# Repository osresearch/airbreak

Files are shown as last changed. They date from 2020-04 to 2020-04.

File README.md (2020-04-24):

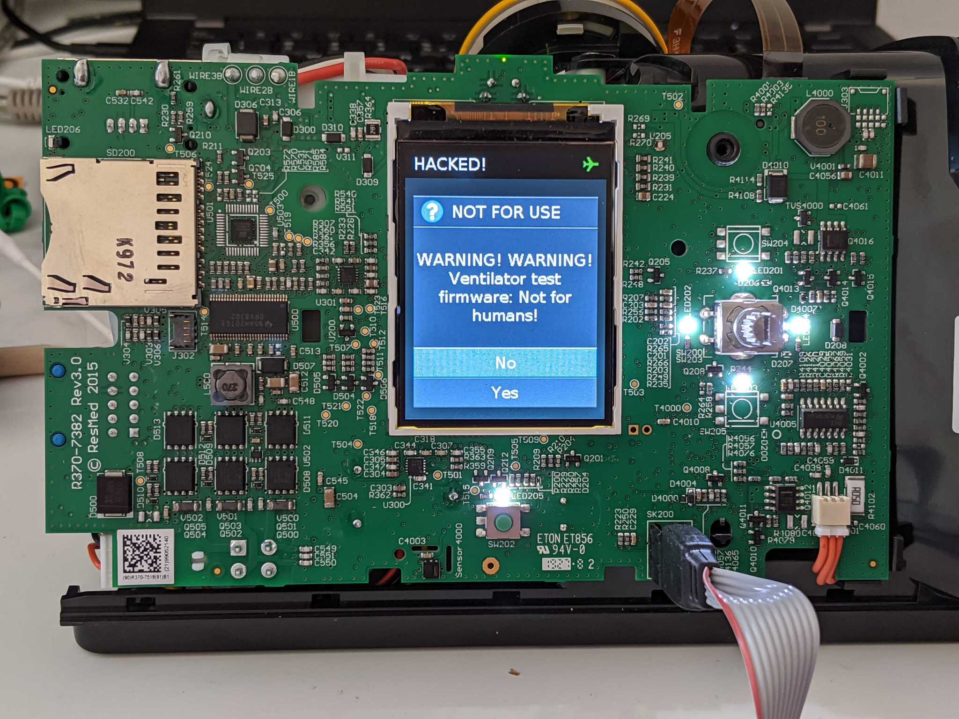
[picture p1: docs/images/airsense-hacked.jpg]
CPAP running custom firmware

# Jailbreaking CPAP machines to make temporary ventilators

This is the README for the internals of ResMed CPAP jailbreak works;
for a high-level overview, see [airbreak.dev](https://airbreak.dev).
The project is [MIT licnsed](LICENSE.txt) and has a [CoC](CODE_OF_CONDUCT.md).
Please review the [Contributor's Guidelines](CONTRIBUTORS.md) before
submitting issues or pull requests.

**This tree does not contain any files that are copyrighted by ResMed.**
You must have a device to extract the firmware from, which is then patched,
and the modified version is re-flashed.

You will need the tools described in [docs/disassembly](docs/disassembly.md).
The `stubs.S` file that has been committed is for SX567-0401. Flashing it on
a different version will likely cause problems.

Extensions can either replace existing functions at fixed addresses,
or can use some of the unused space in the image.
The `Makefile` has a short explanation of how to do this; the
`patch-airsense` file will also need to be updated to patch the
binary file into the firmware.

# Helpful GDB commands:

Start `gdb`, connect to the OpenOCD server and disassemble the current address:
```
gdb-multiarch -iex 'target remote localhost:3333'
display/i $pc
```

Reboot the device and halt before running any code:
```
mon reset halt
```

Unlock the STM32 and flash the new firmware into it:
```
mon stm32f2x options_write 0 0x2c ; reset halt ;  flash write_image erase stm32-unlocked.bin 0x8000000
```

Read the Therapy Manager floating point variables, or a specific one like the target
pressure (`0x2d`):
```
x/200f 0x2000e948
x/f (0x2000e948 + 4 * 0x2a)
```

Read the Therapy Manager integer variables, or a specific one like the current mode (`0x6F`):
```
x/200xw 0x2000e750
x/xw (0x2000e750 + 4 * 0x6F)
```

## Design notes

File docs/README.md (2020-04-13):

CPAP running custom firmware
# Airbreak: jailbreak your CPAP device

In light of the COVID-19 crisis and resultant shortage of medical equipment,
[hospitals have been using BiPAP (BIlevel Positive Airway Pressure) machines as non-invasive ventilators](https://health.mountsinai.org/blog/mount-sinai-turns-hundreds-of-machines-for-sleep-apnea-into-hospital-ventilators-shares-instructions-worldwide/),
and [several groups](https://github.com/PubInv/covid19-vent-list) are currently working on ventilator designs that involve a converted BiPAP.
CPAP devices are cheaper, more widely available, and similar electrically and mechanically. However, they are lacking in some features that the physicians require and,
according to their manufacturer, CPAP machines "[*would require significant rework in order to function as a ventilator*](https://www.resmed.com/en-us/covid-19/)".
other respiratory disorders.

What we have done it to "*jailbreak*" the the Airsense 10 CPAP (Constant
Positive Airway Pressure) machine, a common, low-cost sleep therapy device
intended to treat sleep apnea, so that it is possible to run additional
tasks on the device to add the features necessary to use the device as
a temporary ventilator.  This can help ease the shortage until more real
ventilators are available.

Our changes bring the Airsense S10 to near feature parity with BiPAP
machines from the same manufacturer, boost the maximum pressure output
available, and provide a starting point to add more advanced emergency
ventilator functionality.

## Disclaimer

While we are consulting with doctors to validate that the modified
firmware works as intended, the codebase in its current form should
be considered a proof of concept and is not intended for use in a
life-support capacity.  Please see the [FAQ](#FAQ) for more information.

No IP belonging to the device manufacturer is hosted in this repository,
nor will it be accepted as a pull request.

## Major features:
* Adds a timed breathing mode that oscillates between high and low pressure (stock firmware is only a single pressure)
* Allows maximum pressure to be increased to 30 cm H2O (stock firmware is 20cm H2O)
* Allows very smooth rapid pressure change rates (stock firmware ramps 1 cm/sec)
* Unlocks all of the vendor modes and tunable configuration parameters
* Access to all of the sensors (flow, pressure, temperature, etc)
* Reads tuning parameters from a memory location accessible over SWD
* Real-time data export over SWD
* Real-time graphs on the screen to show an immediate history of data

## Features under development:
* Closed loop air pressure control with backup respiration rates ("VAPS" mode)
* Visual and audible alarms when flow stoppage or leakage rates are detected
* GPIO interface with other systems

# FAQ

## What's the difference between the CPAP and BiPAP machines?
The Airsense 10 that we have modified is a low cost sleep therapy device that
provides a *Constant* air pressure to help with sleep apnea and other disorders.
The BiPAP machines can produce two levels of pressure, which allows them to
be used a temporary ventilators.  Adding a function to the existing firmware
that alternate between pressures allows the CPAP to effectively function
similar to a BiPAP system.

## Can this be used to treat COVID patients?
We want to be very clear here: this modified firmware should not be
flashed on CPAP machines and used to treat COVID patients immediately.
The firmware that we've developed is an effective demonstration of
the capability, and while it has been reviewed and validated by expert
researchers, biomedical engineers, and clinical pulmonologists, it has
not yet been put through FDA approval.  Additionally, the
[Mt Sinai's protocols for off-label non-invasive ventilation](https://health.mountsinai.org/wp-content/uploads/sites/14/2020/04/NIV-to-Ventilator-Modification-Protocol-v1.02-for-posting.pdf)
require additional modifications such as viral filter and remote control
before the machines are ready for clinical use.

## Could this sort of hack alleviate the shortage of ventilators?
If the manufacturers developed their own firmware updates, or the FDA
approves the jailbroken ones, this could have an extremely large role
in bridging the ventilator shortage gap.
There are millions of unused or underutilized CPAP and BiPAP devices sitting in
closets in America, and roughly another 500,000 units in warehouses in
the country.  These devices can be used as an alternate ventilator, for
low-resource hospitals who are still waiting for the hospital ventilators
to arrive.

## Could this go through FDA approval?
If there were no other option it could, but we believe that the best
route for rolling out these upgrades is to work with the manufacturers
to use their resources to validate and distribute these upgrades safely
and at scale.  There are three main factors at play here:

* The first is a regulatory/safety one:  Under the recently-released
FDA guidance on hardware and software modification of CPAP and BiPAP
devices to treat COVID patients, the manufacturer has a carte blanche
to release an updated version of their firmware for their own devices
without requiring explicit FDA approval -- they are in the best position
from a technical, expertise, safety and regulatory perspective.

* The second is a practical one:  There are lots of different models of
CPAP and BiPAP devices, and reverse-engineering is a slow and painful
process. We modified the most common model of CPAP in America, but to
get lots of ventilators quickly, you'd need a firmware modification for
every mode of CPAP. What we've found in our work is that the work needed
for the manufacturer to implement these upgrades is pretty minimal --
the manufacturer has access to the source code, to the schematics,
and to the engineers who are intimately familiar with physiology and
safety standards.  We've found that, in many cases, the bulk of the
work is already done and through FDA, like the iVAPS menu that
is in the firmware on the ResMed Airsense device.  Even if other
manufacturers had not written a line of code for their CPAP models, the
simple pressure-control ventilator mode that we were able to implement
is very simple to develop, is designed to work on every CPAP device in
existence, and would be a very low technology and regulatory barrier
for manufacturers who have the right people and resources.

* The third is related to making these jailbreaks at scale:  We could take
in every unused CPAP device in the country, [unscrew the case and
re-flash the firmware](Installation).  It's slow and expensive but could
be solved with lots and lots of people.  The thing is, of the 8 million
CPAPs in the country, almost all 5 million shipped over the last 3 years
have a cellular IoT connection that is always on, reporting back usage
information to the doctors and the insurance companies.  That cellular
connection also has over-the-air upgrade capability that can only be
accessed from within the IT infrastructure of the device manufacturers.
This is a big deal -- it means that they can selectively upgrade, by
serial number, specific units to function as ventilators, without having
to open them up -- it can all work over the air.

## So what's the point?
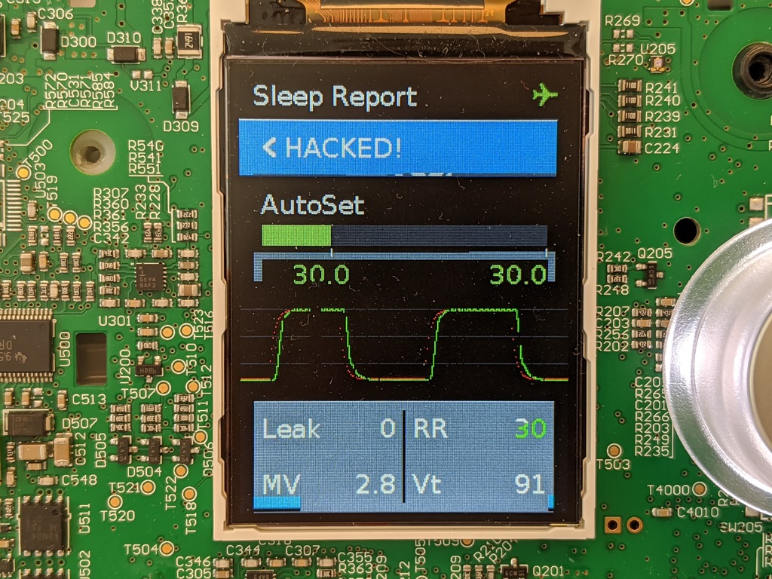
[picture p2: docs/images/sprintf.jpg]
Onscreen graphs


What our firmware does is show that it is possible to re-program these
devices in a way that doctors can use to effectively ventilate COVID
patients. We have been able to confirm the functionality of the devices
in instrumented patient circuits operated by experts in pulmonological
measurement. And there are doctors who agree that, if they had an
FDA-approved machine that could that can do what these machines are doing,
then they could use them to clinically ventilate COVID patients in an ICU.

We do have a path to get this firmware through FDA, and we would apply for
FDA approval under the Emergency Use Authorization if the manufacturers
absolutely refused to cooperate, but the safest and best path is for
the manufacturers to enable this upgrade on their own.

Device owners can also use these tools to write their own [extensions to customize
their devices for their needs](info/extensions), similar to [Magic Lantern](https://magiclantern.fm)
for cameras, as well as the better understand their own therapy by gaining
access to the sensors on the device.  They can add features like the on-screen
graphs shown above, or integrate external systems through the expansion port.

# Evaluation

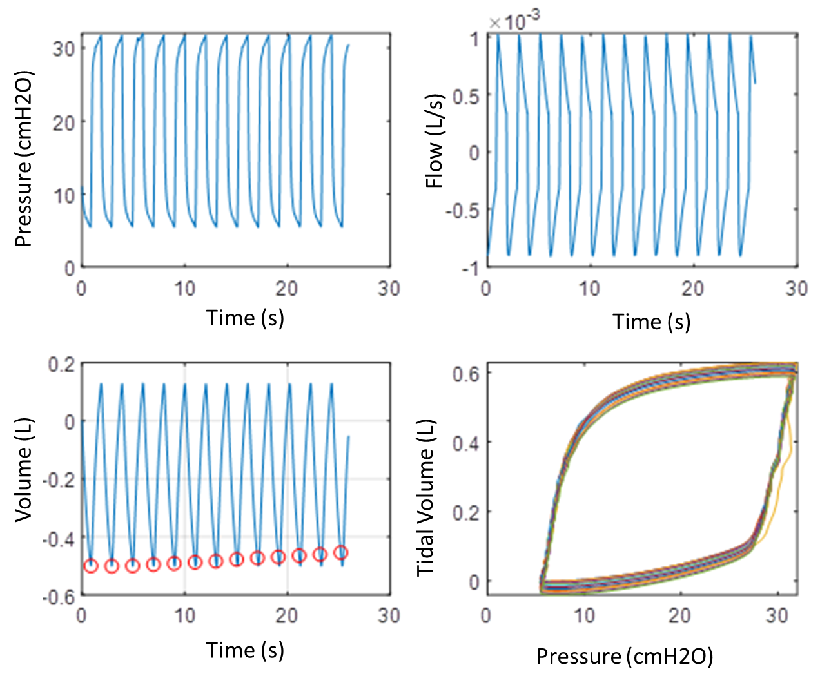
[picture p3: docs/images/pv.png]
PV curves


To be written.  Currently the modified firmware is being evaluated by
research labs and pulmnologists.  There are other pieces necessary to
use the devices in a clinical setting, such as filter traps, O2 inputs,
alarms, etc.

[Mt Sinai's BiPAP protocols for non-invasive ventilation](https://health.mountsinai.org/wp-content/uploads/sites/14/2020/04/NIV-to-Ventilator-Modification-Protocol-v1.02-for-posting.pdf)
provide a roadmap for how these modified CPAP devices could be used.

# More details

* [Installation guide](/disassembly)
* [Writing extensions](info/extensions)

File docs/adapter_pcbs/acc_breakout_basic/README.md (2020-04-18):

# Accessory Board Edge Connector Breakout

Small PCB that fits into the accessory port on the side. Originally designed for building out the monitor USART connection.

This board is designed to be millable on a Bantam PCB mill so makes some odd-looking PCB design choices. As there is no PTH you'll notice headers were put on each side in photo below. You will need to use both 1/32" and 1/64" end mills.

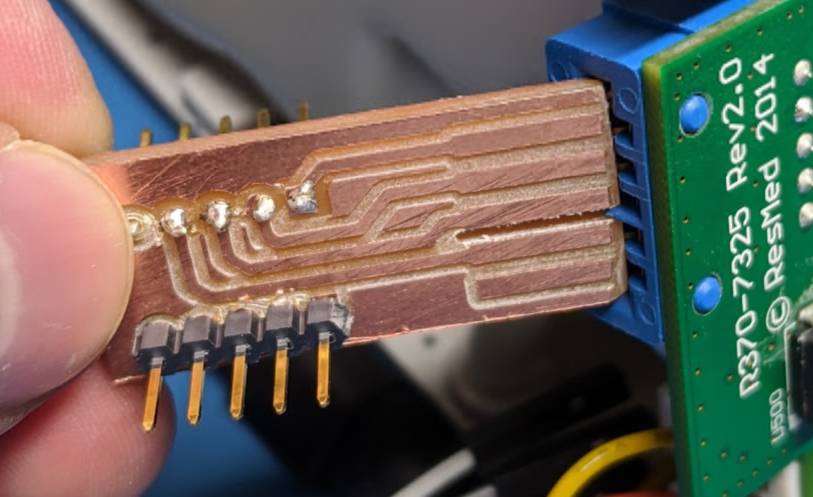
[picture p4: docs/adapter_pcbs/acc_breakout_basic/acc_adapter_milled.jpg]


You can freely send the board away to be made of course too.

**WARNING**: Sanding FR4 material creates dangerous dust. If you need to bevel the edge use appropriate precautions such as sanding under water.

## PCB Source Format

PCB design files are in Altium Designer source (sorry).

### Sizes

The card edge dimensions are roughly based on a standard card-edge, see [example connector spec that includes PCB sizes](https://media.digikey.com/pdf/Data%20Sheets/Panasonic%20Electric%20Works%20PDFs/AXC.pdf).

Board should be 15 mm width (or a little less). The gerber files have a small board outline width to ensure Bantam software gives correct edge size (otherwise may mill on outside edge).

The connectors are on 2.54mm (0.100" grid). Other spacing shown below:

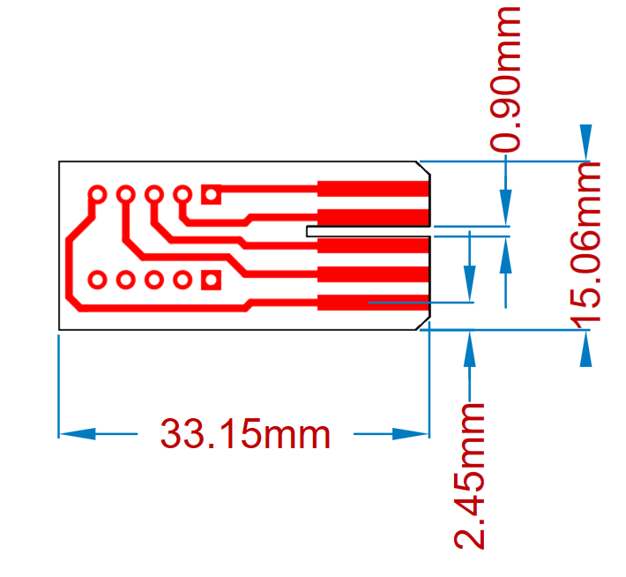
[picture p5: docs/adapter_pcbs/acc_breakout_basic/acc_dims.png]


## Pinout Notes

See pinout stored in rest of project, the following shows pinout of hedaers relative to pin numbers marked on main-board part number:

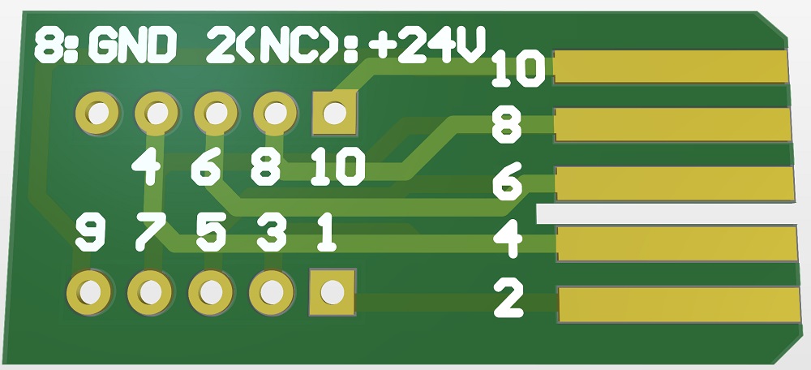
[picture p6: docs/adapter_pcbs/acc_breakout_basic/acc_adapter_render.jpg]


Note that pin 2 is +24V and is NOT connected to the header. Add the wire if you need it, but assumed more people will be sad-face about brushing +24V against their 3.3V USART adapter than would use the +24V for debug.

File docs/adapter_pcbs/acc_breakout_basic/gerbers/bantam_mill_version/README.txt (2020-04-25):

These gerbers are designed to work with the Bantam mill.

They use 2.3 format, with very small edge (GM1) layer.

You will need 1/32" and 1/64" end mills to mill this.

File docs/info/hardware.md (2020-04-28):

# Airsense S10 Hardware

This page aggregates hardware details about the Airsense S10 electronics
and other information that may be relevant to the reverse engineering process.

## FCC Filings

One crucial reverse engineering resource is the
[FCC documentation for the AirSense S10](https://fccid.io/2ACHL-AIR104G), which
includes external and internal schematics and user manuals.

[The FCC filings for the AirCurve BiPAP](https://fccid.io/2ACHL-A10STA3G),
currently in use as an emergency ventilator, shows very similar electronics.

## Clinical Manuals

[Clinical manuals](https://www.manualslib.com/brand/resmed/medical-equipment.html)
for the assisted-breathing devices from this manufacturer provide a great deal
of insight into the various models in the AirSet and AirCurve lines, as well as
the ventilation features available in each one.
Many of the menu options restricted to other models can be enabled by flipping
configuration bits in the firmware.

## Components 

Here are some of the components on the AirSense S10 

Main PCB

| Part  		| Part No. | Manufacturer | Reference | Additional |
| ---			| --- | --- | --- | --- |
| Main uC		| STM32F405ZGT6 (LQFP144) | STMicroelectronics | [Datasheet](https://www.st.com/resource/en/datasheet/stm32f405zg.pdf) | [Reference Manual](https://www.st.com/resource/en/reference_manual/cd00190271-stm8s-series-and-stm8af-series-8bit-microcontrollers-stmicroelectronics.pdf) | 
| Aux uC		| STM8S005 (TQFP48) |  STMicroelectronics | [Datasheet](https://www.st.com/content/ccc/resource/technical/document/datasheet/21/5a/57/8b/f4/49/4a/12/DM00037613.pdf/files/DM00037613.pdf/jcr:content/translations/en.DM00037613.pdf)  | [Reference Manual](https://www.st.com/resource/en/reference_manual/cd00190271-stm8s-series-and-stm8af-series-8bit-microcontrollers-stmicroelectronics.pdf) | 
| Power watchdog IC	| POWR605  | Lattice | [Datasheet](http://www.latticesemi.com/~/media/LatticeSemi/Documents/DataSheets/ProcessorPM-POWR605DataSheet.pdf) | Monitors pressures - see notes below|
| Main Pressure Sensor  | NPA-300M-015A | Amphenol | [Datasheet](https://amphenol-sensors.com/en/component/edocman/212-novasensor-npa-surface-mount-pressure-sensors-datasheet/download?Itemid=8429) | Operates in analog mode |
| Differential Pressure Sensor | SDP8xx | Sensirion | [Datasheet](https://www.sensirion.com/en/about-us/company/technology/cmosens-technology-for-gas-flow/) | Digital mode, manifold mount |
| Programming Header	| TC2050-IDC | Tag-Connect LLC | [DigiKey](https://www.digikey.com/product-detail/en/tag-connect-llc/TC2050-IDC/TC2050-IDC-ND/2605366) | 
| Motor Driver | DRV8302 | Texas Instruments | [DigiKey](https://www.digikey.com/product-detail/en/tag-connect-llc/TC2050-IDC/TC2050-IDC-ND/2605366) | 
| Serial EEPROM | M95M02 | STMicroelectronics | [Datasheet](https://www.st.com/resource/en/datasheet/m95m02-dr.pdf) | 
| LCD | TM024HDZ29 | Tianma | [Similar datasheets](https://www.beyondinfinite.com/product/lcd/tianma_lcd_display.html) | [Closest we could find](https://z3d9b7u8.stackpathcdn.com/pdf-down/T/M/0/TM024HDH30-01-Tianma.pdf)|
| Relay Driver | A2550 | Allegro | [Datasheet](https://www.allegromicro.com/~/media/Files/Datasheets/A2550-Datasheet.ashx) | Function unknown; accessory? | 
| Logic Voltage Regulator (x2) | ISL9000A | Renesas | [Datasheet](https://www.mouser.ca/datasheet/2/698/isl9000a-1529533.pdf) | Generates 3.3v and 5v logic voltages | 
| Top Switch | B3F-3125 | Omrom | [Digikey](https://www.digikey.com/product-detail/en/omron-electronics-inc-emc-div/B3F-3125/SW851-ND/368368) | In case switch needs to be replaced (confirmed exact fit)|

Cellular Module & Antenna (CAM) Board

| Part  		| Part No. | Manufacturer | Reference | Additional |
| ---			| --- | --- | --- | --- |
| Main uC		| R5F5210ABDFP | Renesas | [Datasheet](https://www.renesas.com/eu/en/doc/products/mpumcu/doc/rx_family/r01ds0041ej0150_rx210.pdf) | LFQFP 100-pin |
| CDMA Radio Module| ce910-dual | Telit | [Datasheet](https://static6.arrow.com/aropdfconversion/1e95506f859937cecfcd3d7fd07cc25d6eab906d/telit_ce910-dual_datasheet.pdf) | [qualcomm qsc1105 chipset](https://fccid.io/RI7CE910-DUAL/Internal-Photos/Internal-Photos-1760716) |
| 3G Radio Module| HE910-D | Telit | [Datasheet](hhttps://www.telit.com/wp-content/uploads/2017/09/160229_DS_HE910.pdf) | [Uknown chipset- FCC photos obscured](https://fccid.io/RI7HE910/Internal-Photos/Internal-Photos-1654391)|
| 4G Radio Module| cinterion els61-us | Gemalto | [Datasheet](https://www.gemalto.com/brochures-site/download-site/Documents/M2M_ELS61_datasheet.pdf) | Cat 1 LTE w/ 2G/3G fallback | 

Alarm Board (Only A10STACD, A10STA3G, AIR104G)

| Part  		| Part No. | Manufacturer | Reference | Additional |
| ---			| --- | --- | --- | --- |
| Main uC		| R5F21358CNFP | Renesas | [Datasheet](https://4donline.ihs.com/images/VipMasterIC/IC/RNCC/RNCCS11762/RNCCS11762-1.pdf) | [Avnet](https://www.avnet.com/shop/emea/products/renesas-electronics/r5f21358cnfp-30-3074457345629542777/) |

## Power Watchdog

The power watchdog IC (POWR605) is a complicated power watch-dog IC. More than just a basic device, it contains:

* 6 DC power monitoring inputs.
* 16 macrocell PLD logic.
* 4 timers.

The 6 inputs have programmable thresholds (despite what the datasheet implies about fixed).

This device is important as appears to be used as a "safety" on pressure sensors. If pressures are too far out-of-spec it will reset the main STM32F407ZG microcontroller. More reverse engineering is needed to understand the exact connection here.

The POWR605 logic should be reprogrammable via the tag-connect header. The following works (but may not be easiest/lowest-cost):

* "Lattice Diamond" programming software.
* Programming Cable supported by above (such as HW-USBN-2B).
* Lattice "PAC-Designer" software.

To read the device, ensure you configure the Lattice Diamond SW to perform a "JEDEC Readback" - the default operation is erase/program/verify. This will then generate a `.jed` file.

From PAC-Designer, create a new project with the POWR605. You can then use the `Import` option to open the `.jed` to see configuration.

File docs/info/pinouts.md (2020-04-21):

# Pinouts

## STM32

| STM32 Pin#	| GPIO	|-| Peripheral	| Pin	| Function | 
| ----- 		| ----  |-| -----     | ----  | -----------	| 
| 34			| PA00	|-| Aux uC	| 47	| WKUP | 
| 37			| PA03	|-| Aux uC	| 47	| USART2_RX | 
| 40			| PA04	|-| 1x2 Header	| 1	|  | 
| 41			| PA05	|-| 1x2 Header	| 2	|  | 
| 100			| PA08	|-| Motor Driver	| 21	| INH_C | 
| 101			| PA09	|-| Motor Driver	| 19	| INH_B | 
| 102			| PA10	|-| Motor Driver	| 17	| INH_A | 
| 105			| PA13	|-| Programming Header	| 2	| SWDIO | 
| 109			| PA14	|-| Programming Header	| 4	| SWCLK | 
| 110			| PA15	|-| EEPROM	| 1	| ~CS | 
| 47			| PB01	|-| POWR605     | 5	| VMON4 | 
| 136			| PB06	|-| LTE header	| 2	| USART1_TX | 
| 137			| PB07	|-| LTE header	| 3	| USART1_RX | 
| 139			| PB08	|-| Diff Pressure Sensor	| 	| SCL | 
| 140			| PB09	|-| Diff Pressure Sensor	| 	| SDA | 
| 69			| PB10	|-| Blue edge connector	| 9	| USART3_TX | 
| 70			| PB11	|-| Blue edge connector	| 7	| USART3_RX | 
| 74			| PB13	|-| Motor Driver	| 22	| INL_C | 
| 75			| PB14	|-| Motor Driver	| 20	| INL_B | 
| 76			| PB15	|-| Motor Driver	| 18	| INL_A | 
| 44			| PC04	|-| Pressure Sensor	| 8	|  | 
| 98			| PC08	|-| SD Card	| 	| DAT0/D0 | 
| 99			| PC09	|-| SD Card	| 	| DAT1/IRQ | 
| 111			| PC10	|-| SD Card	| 9	| DAT2/NC | 
| 112			| PC11	|-| SD Card	| 1	| DAT3/~CS | 
| 113			| PC12	|-| SD Card	| 5	| SCK | 
| 8				| PC14	|-| OSC	| 	| OSC32_IN | 
| 9				| PC15	|-| OSC	| 	| OSC32_OUT | 
| 114			| PD00	|-| SRAM	| 9	| IO_2 | 
| 115			| PD01	|-| SRAM	| 10	| IO_3 | 
| 116			| PD02	|-| SD Card	| 2	| CMD/DI | 
| 118			| PD04	|-| SRAM	| 41	| ~OE | 
| 119			| PD05	|-| SRAM	| 17	| ~WE | 
| 77			| PD08	|-| SRAM	| 36	| IO_13 | 
| 78			| PD09	|-| SRAM	| 37	| IO_14 | 
| 79			| PD10	|-| SRAM	| 38	| IO_15 | 
| 80			| PD11	|-| SRAM	| 18	| ADDR_16 | 
| 81			| PD12	|-| SRAM	| 23	| NC | 
| 85			| PD14	|-| SRAM	| 7	| IO_0 | 
| 86			| PD15	|-| SRAM	| 8	| IO_1 | 
| 141			| PE00	|-| SRAM	| 39	| ~LB | 
| 142			| PE01	|-| SRAM	| 40	| ~UB | 
| 1				| PE02	|-| Motor Driver	| 5	| nOCTW | 
| 2				| PE03	|-| Motor Driver	| 6	| nFAULT | 
| 3				| PE04	|-| LCD	| 12	|  | 
| 4				| PE05	|-| SD Card	| 6 (on board)	| Pulled low when SD card inserted | 
| 58			| PE07	|-| SRAM	| 13	| IO_4 | 
| 59			| PE08	|-| SRAM	| 14	| IO_5 | 
| 60			| PE09	|-| SRAM	| 15	| IO_6 | 
| 63			| PE10	|-| SRAM	| 16	| IO_7 | 
| 64			| PE11	|-| SRAM	| 29	| IO_8 | 
| 65			| PE12	|-| SRAM	| 30	| IO_9 | 
| 66			| PE13	|-| SRAM	| 31	| IO_10 | 
| 67			| PE14	|-| SRAM	| 32	| IO_11 | 
| 68			| PE15	|-| SRAM	| 35	| IO_12 | 
| 10			| PF00	|-| SRAM	| 5	| ADDR_0 | 
| 11			| PF01	|-| SRAM	| 4	| ADDR_1 | 
| 12			| PF02	|-| SRAM	| 3	| ADDR_2 | 
| 13			| PF03	|-| SRAM	| 2	| ADDR_3 | 
| 14			| PF04	|-| SRAM	| 1	| ADDR_4 | 
| 15			| PF05	|-| SRAM	| 44	| ADDR_5 | 
| 49			| PF11	|-| Button/Encoder	| Close to D4007 Label	|  | 
| 53			| PF13	|-| SRAM	| 42	| ADDR_7 | 
| 54			| PF14	|-| SRAM	| 27	| ADDR_8 | 
| 55			| PF15	|-| SRAM	| 26	| ADDR_9 | 
| 56			| PG00	|-| SRAM	| 25	| ADDR_10 | 
| 57			| PG01	|-| SRAM	| 24	| ADDR_11 | 
| 92			| PG07	|-| Home Button	| 	|  | 
| 93			| PG08	|-| Power Button	| 	|  | 
| 127			| PG12	|-| POWR605	| 15    | IN_OUT5 | 
| 128			| PG13	|-| POWR605	| 17    | IN_OUT4 | 
| 23			| PH00	|-| OSC	| 1	| OSC_IN | 
| 24			| PH01	|-| OSC	| 2	| OSC_OUT | 

## Accessory Connector

The accessory connector is a blue edge-connect PCB connector. See the example pcb for the layout of a mating PCB. The following table matches the pinout when looking into the side connector:

| Pin # | Function |   xxx  |  Pin # | Function  |
| ----- | -------- | ------ | -----  | --------- |
|   9   | TX (Out) | ------ |   10   |  ?        |
|   7   | RX (In)  | ------ |   8    |  GND      |
|   5   | ?        | ------ |   6    |  ?        |
|   3   | ?        | ------ |   4    |  ?        |
|   1   | ?        | ------ |   2    |  +24V     |

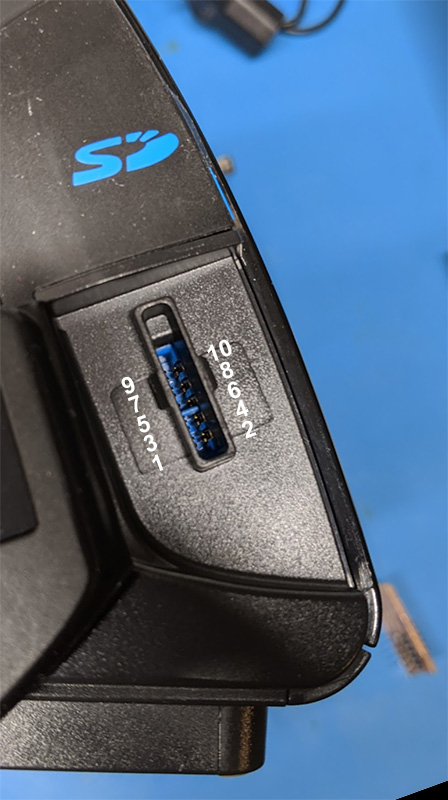
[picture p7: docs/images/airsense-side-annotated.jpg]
Photo of Side Connector with Pin Numbering


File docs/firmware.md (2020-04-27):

# Firmware 

### Connecting to Device

!!! Note
	If you are using Windows, the steps in this section
	will be slightly different. Please see the [Windows
	guide](info/windows.md) for more information.

We are going to use the open-source [OpenOCD](http://openocd.org) debug
interface to access the device.

First, make sure [this repository](https://github.com/osresearch/airbreak)
is cloned and located in your working directory.

Make sure your programmer is [attached to the PCB](/disassembly/#wiring),
then start OpenOCD.  If you are using a programmer other than the ST-Link/V2, you
will need to select the correct interface.

```sh
sudo openocd -f interface/stlink-v2.cfg -f 'tcl/airsense.cfg'
```

If your device is connected properly, you should see a bunch of output, ending with:
```sh
Info : stm32f4x.cpu: hardware has 6 breakpoints, 4 watchpoints
```

In another terminal, connect to the OpenOCD server:

```sh
telnet localhost 4444
```

Once your OpenOCD console is successfully connected, you can continue to the next step.

## Dumping Vendor Firmware

!!! Warning
	This step is mandatory. Each subsequent step requires an
	original copy of the device firmware to be present in the working
	directory. With an original copy of the firmware, the device can
	always be restored to factory settings. If you lose the original
	firmware, you risk bricking your device!

Type the following into your OpenOCD console:
```sh
dump
```
After several seconds, your device's main firmware
should be backed-up to `stm32.bin` in the working directory - it should
be exactly 1MB.

## Building Alternate Firmware

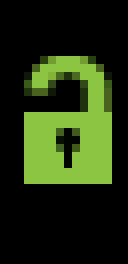
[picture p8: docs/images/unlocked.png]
Unlocked icon


In a third terminal window, patch the extracted firmware at
`stm32.bin` with the `patch-airsense` script.  This will 
unlock the vendor modes and configuration bits.

```
./patch-airsense stm32.bin stm32-unlocked.bin
```

There are several features configurable via the `patch-airsense`
script, some of which are simple binary patches and some of which
require a 32-bit ARM toolchain. Set them as desired per the
documentation [here](../info/firmware-docs).

The script might fail if the hashes of your extracted firmware do not
match the one that it expects (currently `SX567-0401`). If you have a
different version, please contact us for how to proceed.

## Flashing

Now reflash the device with the modified firmware by going back to the
OpenOCD console terminal and running:

```sh
flash_new stm32-unlocked.bin
```

This step takes around 20 seconds and the device should
reboot afterwards.

## Testing

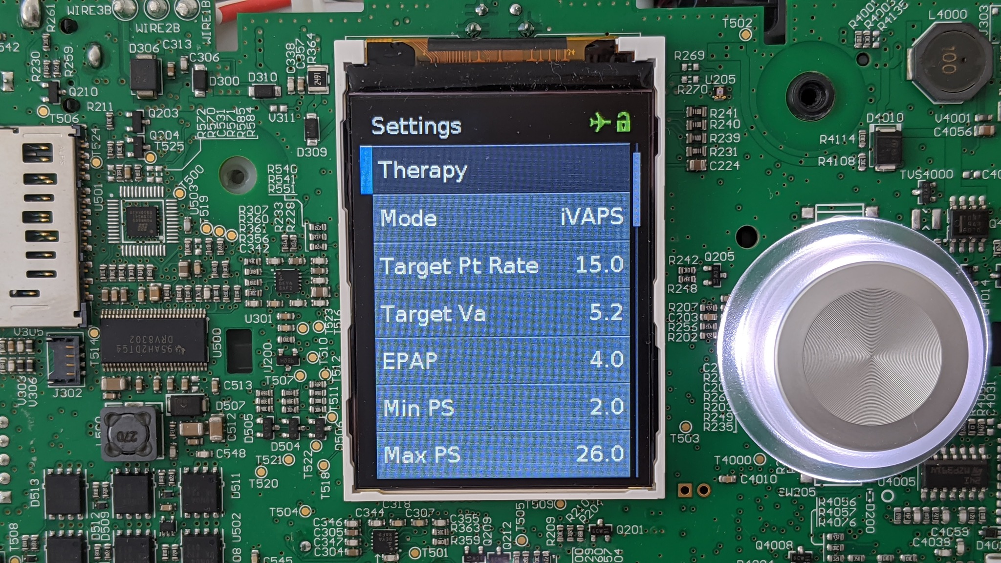
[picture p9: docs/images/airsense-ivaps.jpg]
iVAPS mode unlocked


After the device has been reflashed and rebooted, you can enter the
clinician menu (hold down the `Home` button while pushing on the knob
for three seconds), and you should be able to select from all of the vendor
modes, including iVAPS and ST.  These modes potentially allow the CPAP device
to immediately be used according to the Mt Sinai BiPAP protocol.

The flashing is a one-time operation.  The programmer can be unplugged and moved to another device. Remember to keep a backup of the vendor firmware.

## Restoring Vendor Firmware

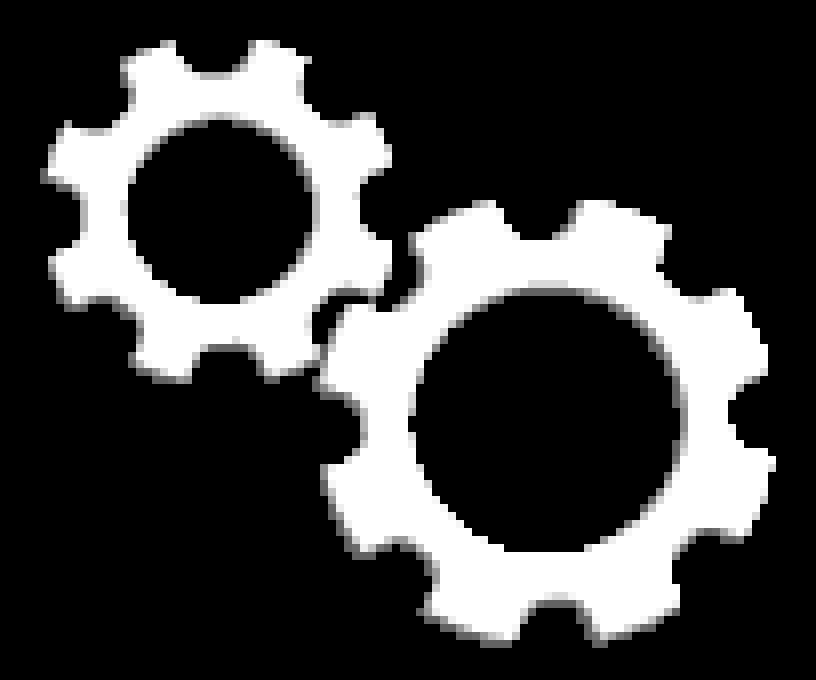
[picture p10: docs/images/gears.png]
Gears icon


In order for the vendor firmware to flash properly, it is necessary
to write variables to the device's backup memory in a certain sequence.
The following OpenOCD command will do that:
```sh
flash_new stm32.bin
```

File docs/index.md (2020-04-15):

CPAP running custom firmware
# Jailbreak your CPAP machine with Airbreak

In light of the COVID-19 crisis and resultant
shortage of medical equipment, [hospitals have developed protocols for
using BiPAP (BIlevel Positive Airway Pressure) machines as non-invasive
ventilators](https://health.mountsinai.org/blog/mount-sinai-turns-hundreds-of-machines-for-sleep-apnea-into-hospital-ventilators-shares-instructions-worldwide/),
the [FDA has approved the use of these modified BiPAP devices as ventilators](https://www.fda.gov/media/136702/download),
and [several groups](https://github.com/PubInv/covid19-vent-list)
are currently working on ventilator designs that involve a
converted BiPAP.  However, CPAP (Constant Positive Airway Pressure) devices
are cheaper, more widely available, and similar both electrically
and mechanically.  Unfortunately, they are lacking in some features that
the physicians require and, according to their manufacturer, CPAP
machines "[*would require significant rework in order to function as
a ventilator*](https://www.resmed.com/en-us/covid-19/)".

What we have done is to "*jailbreak*" the the Airsense 10 CPAP
machine, a common, low-cost sleep therapy device
intended to treat sleep apnea, so that it is possible to run additional
tasks on the device. These new tasks add the features and adjust the range of
parameters that make it possible, along with extra equipment like viral filters,
to use the device as a temporary ventilator.
This can help ease the shortage until more real ventilators are available.

Our changes bring the Airsense S10 to near feature parity with BiPAP
machines from the same manufacturer, boost the maximum pressure output
available, and provide a starting point to add more advanced emergency
ventilator functionality.

## Disclaimer

While we are consulting with doctors to validate that the modified
firmware works as intended, the codebase in its current form should
be considered a **proof of concept** and is
**not intended for use in a life-support capacity**.
Additional equipment like **viral filters** and **monitoring alarms**
are also required.
Please see the [FAQ](#faq) for more information.

No IP belonging to device manufacturers is hosted in this repository,
nor will it be accepted as a pull request.

## Major features
* Adds a Pressure Control Ventilator (PCV) mode that oscillates between high and low pressure at a configurable breathing rate (stock firmware supports only a single pressure, with no breath rate control).
* Allows maximum pressure to be increased to 30 cm H<sub>2</sub>O, as required by clinical protocols (stock firmware is limited to 20cm H<sub>2</sub>O).
* Allows smooth rapid pressure change rates for respiration rates up to 30 breaths per minute (stock firmware changes pressure at less than 1 cm/sec).
* Unlocks all of the vendor modes and tunable configuration parameters, including ST and iVAPS modes present in the firmware.
* Provides access to all of the sensors (flow, pressure, temperature, tidal volume, minute ventilation, etc).
* Displays real-time graphs on the screen to show an immediate history of sensor data.

## Development features
* Visual and audible alarms when flow stoppage or leakage rates are detected.
* Closed loop air volume control with backup respiration rates and supplemental O<sub>2</sub>.
* GPIO interface with other systems.
* Display statistics in conformance with [Rapidly Manufactured Ventilator Standards](https://docs.google.com/spreadsheets/d/17EJ9TN6O1wqP4c-lIn5hbmuMRrto7M_KXHf17zjNSLk/edit#gid=704151435).

## FAQ

### What's the difference between CPAP and BiPAP machines?

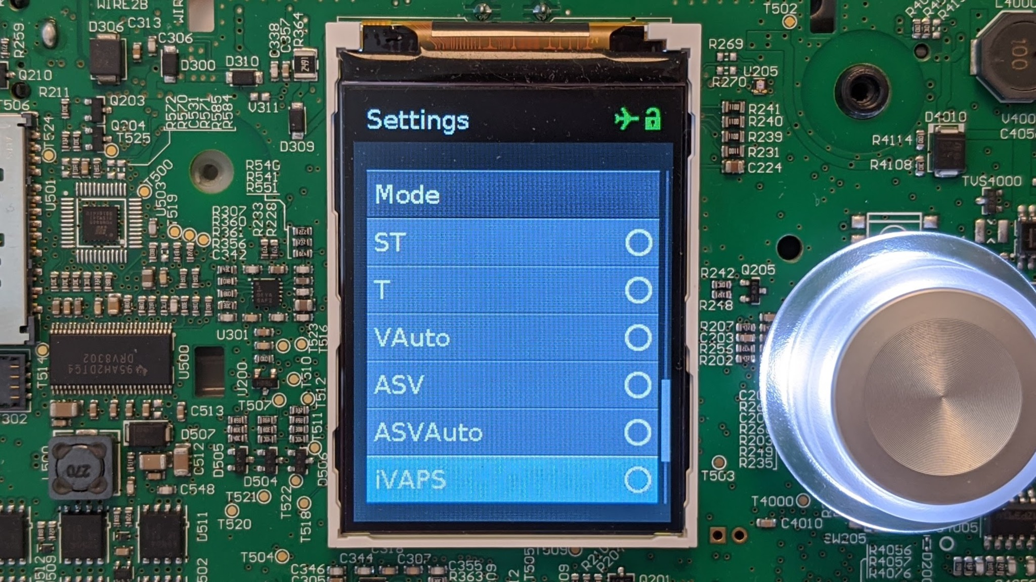
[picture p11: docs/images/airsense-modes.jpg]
Therapy mode menu on an unlocked Airsense 10 CPAP machine


The Airsense 10 that we have modified is a low cost sleep therapy device
that provides a *Constant* Positive Air Pressure to help with sleep apnea and
other disorders.  This CPAP mode applies constant pressure to the lungs,
but it does not ventilate, or let air move in and out of the lungs.

The BiPAP machines are more capable devices to treat sleep apnea
and COPD that provide *Bi-level* Positive Airway Pressure.  Bi-level
pressure *triggers* on patient breaths, applying higher pressure when
the patient tries to breathe in, and a lower pressure when the patient
tries to exhale.  This is what's called a *support* mode, which provides
additional pressure support to a patient's natural breathing.

These differences apply to the devices as they function **out of the box**.
Our work indicates that the actual difference between a low-end
CPAP device and a high-end iVAPS device is just a **software upgrade**.
The CPAP machines have many of the same sensors as the more
expensive models, and the Airsense 10 CPAP devices include in their
firmware all of the other modes, such as iVAPS and BiPAP-ST.
When we unlock that mode in software, the CPAP device functions like a
much more capable and expensive iVAPS device.

This idea, that the difference between CPAP and BiPAP machines is a
*software* change rather than a *hardware* change, is at the root of
our work.  If the common, highly distributed CPAP devices could have a
software upgrade that turns them into iVAPS or BiPAP-ST devices capable
of ventilating COVID patients, that would be a huge boon to the hospitals
and health care workers around the world who are struggling with a lack
of ventilators or alternatives to treat the influx of COVID patients.

Adding a homebrew function to the existing firmware that alternates
between pressures with a configurable delay allows the CPAP to effectively
function as a Pressure Control Ventilator (PCV) for sedated patients.
Enabling the vendor-provided iVAPS mode,
along with [further customization and new extensions](info/extensions),
should make the devices even more flexible and suitable for clinical use.

### Can jailbroken CPAP devices be used to treat COVID patients?

We want to be very clear here: this modified firmware should **not** be
flashed on CPAP machines and used to treat COVID patients immediately.
The firmware that we've developed is an effective demonstration of
the capability, and while it has been [reviewed and validated by expert
researchers, biomedical engineers, and clinical pulmonologists](evaluation), it has
not yet been put through FDA approval.  Additionally, the
[Mt Sinai's protocols for off-label non-invasive ventilation](https://health.mountsinai.org/wp-content/uploads/sites/14/2020/04/NIV-to-Ventilator-Modification-Protocol-v1.02-for-posting.pdf)
require additional modifications such as viral filter and remote control
before the machines would be ready for clinical use.

### Could hacked machines alleviate the shortage of ventilators?
If the manufacturers developed their own firmware updates, or the FDA
approves our jailbroken firmware, this could have an extremely large role
in bridging the ventilator shortage gap.
There are millions of unused or underutilized CPAP and BiPAP devices sitting in
closets in America, and roughly another 500,000 units in warehouses in
the country.  These devices can be used as an alternate ventilator, for
low-resource hospitals who are still waiting for the hospital ventilators
to arrive.

### Could homebrew firmware go through FDA approval?
Airsense 10 CPAP machine with iVAPS configuration menu

If there were no other option, our firmware could go through FDA approval,
but we believe that the best route for rolling out these upgrades is
to work with the manufacturers to use their resources to validate and
distribute these upgrades safely and at scale.  There are three main
factors at play here:

* The first is a regulatory/safety one:  Under the recently-released
FDA guidance on hardware and software modification of CPAP and BiPAP
devices to treat COVID patients, the manufacturer has carte blanche
to release an updated version of their firmware for their own devices
without requiring explicit FDA approval -- they are in the best position
from a technical, expertise, safety and regulatory perspective.

* The second is a practical one:  There are many different models of
CPAP and BiPAP devices, and reverse-engineering is a slow and painful
process. We modified the firmware on the most common model of CPAP in
America in about a week, but to get lots of ventilators quickly, you'd
need a firmware modification for every mode of CPAP.
What we've found in our work is that the work needed
for the manufacturer to implement these upgrades is pretty minimal --
the manufacturer has access to the source code, to the schematics,
and to the engineers who are intimately familiar with physiology and
safety standards.  We've found that, in many cases, the bulk of the
work has already gone through FDA approval, like the iVAPS menu that
is in the firmware on the ResMed Airsense device shown above.  Even if other
manufacturers had not written a line of code for their CPAP models, the
pressure-control ventilator mode that we were able to implement
is very simple to develop, designed to work on every CPAP device in
existence, and would be a very low technology and regulatory barrier
for manufacturers with the right people and resources.

* The third is related to making these jailbreaks at scale:  We could take
in every unused CPAP device in the country, [unscrew the case](disassembly)
and [re-flash the firmware](firmware).  It's slow and expensive but could
be solved with lots and lots of people.  The thing is, of the 8 million
CPAPs in the country, almost all 5 million shipped over the last 3 years
have an always-on cellular IoT connection, reporting back usage
information to doctors and insurance companies.  That cellular
connection also has over-the-air upgrade capability that can only be
accessed from within the IT infrastructure of the device manufacturers.
This is a big deal -- it means that they can selectively upgrade, by
serial number, specific units to function as ventilators, without having
to open them up -- it can all work over the air.

### So what's the point?
Onscreen graphs

What our firmware does is show that it is possible to re-program these
devices in a way that doctors can use to effectively ventilate COVID
patients. We have been able to confirm the functionality of the devices
in instrumented patient circuits operated by experts in pulmonological
measurement. And there are doctors who agree that, if they had an
FDA-approved machine that could that can do what these machines are doing,
then they could use them to clinically ventilate COVID patients in an ICU.

We do have a path to get this firmware through FDA, and we would apply for
FDA approval under the Emergency Use Authorization if the manufacturers
absolutely refused to cooperate, but the safest and best path is for
the manufacturers to enable this upgrade on their own.

Separately from the very pressing COVID issues, Airbreak allows
CPAP device owners to write their own [extensions to customize their
devices for their needs](info/extensions), similar to what the [Magic
Lantern](https://magiclantern.fm) firmware does for cameras.  They can
add features like the on-screen graphs shown above, or integrate external
systems through the expansion port.  Additionally, these tools allow
the owners and users to gain a better understand their own therapy by
gaining access to the sensors on the device.

## More details

* [Laboratory evaluation](evaluation)
* [Disassembly and wiring instructions](/disassembly)
* [Firmware flashing guide](/firmware)
* [Writing extensions](info/extensions)
* [github.com/osresearch/airbreak](https://github.com/osresearch/airbreak)
* [info@airbreak.dev](mailto://info@airbreak.dev)

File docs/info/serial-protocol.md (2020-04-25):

# Serial Protocol

The unit has a serial port at 57600 baud available on accessory-board (see [pinouts](pinouts.md) for pinouts, and [adapter pcbs](../adapter_pcbs) for physical information).

This collects some in-progress notes. If you just need to talk a unit for experimentation, you might consider instead the working 'serial monitor' replacement code until this is figured out more.

This is assumed to be used with the [TX Link](https://www.resmed.com/epn/dam/documents/products/titration/tx-link/quick-setup-guide/tx-link_quick-setup-guide_glo_eng.pdf) device. Information is only available on the S9 version, but the interface connector looks to be the same (not confirmed).

## Protocol Notes

The device will respond to some commands starting with a `U`. The code can be seen checking for a 0x55 in parts, so this makes sense as some sort of Sync character. Sending for example:

	UV

Will have the unit respond with:

	UE010 = 6011807B

The `807B` is a CRC-16 of the preceding ASCII data:
	
	import crcmod
	import crcmod.predefined
	crc_func = crcmod.predefined.mkCrcFun('crc-ccitt-false')
	crc = crc_func(b"UE010 = 6011")
	print(str(hex(crc)))

Sending `U` + most characters seems to trip the above response. Some do not respond however suggesting there is "subcommands" that are waiting for more data:

	UQA seems to give no response.
	UP{A-T,V-Z,0-9} seems to give no response.
	ULA seems to give no response.

The various "response codes" can be seen in the firmware. Looking at firmware suggests some commands looking for 3-character code. For example:

	UL01B

(you may need to send it a few times) seems to trip response code `600C`. In the firmware, it can be seen that a 3-character string is converted to hex (i.e., 01B in the example becomes 0x1B).

## Firmware Notes

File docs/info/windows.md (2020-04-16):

# Windows Instructions

*WARNING:* Be aware that the STM32F series has a 'code read protection' feature. The only legitimate way to 'disable' this is to perform a chip erase. Current devices investigated do not have this enabled - but if this feature was enabled, you will receive an error message that may say something simple such as "Do you want to disable read protection?". If you perform this action, you will have erased the firmware.

## Programming with ST-Link Utility

If using a legitimate or fake ST-Link/V2, you will find it most convient to use the ST-Link utility for basic operation (read/write).

To do this, download the ST-Link utility at: https://www.st.com/en/development-tools/stsw-link004.html. Scroll down the page until the "Get Software" button is visible.

## Reading

You must use the "Command Line Interface" to read flash (the option is not in the ST-Link GUI as of the latest version). Open a command prompt on Windows, and run the following two commands. The first one does the read, the second one verifies it:

	ST-LINK_CLI.exe -c -dump 0x08000000 0x100000 stm32.bin
	ST-LINK_CLI.exe -CmpFile stm32.bin 0x8000000

## Writing

You can either use the GUI to do the writing, or run the following command:

	ST-LINK_CLI.exe -ME -P stm32-unlocked.bin 0x08000000 -V

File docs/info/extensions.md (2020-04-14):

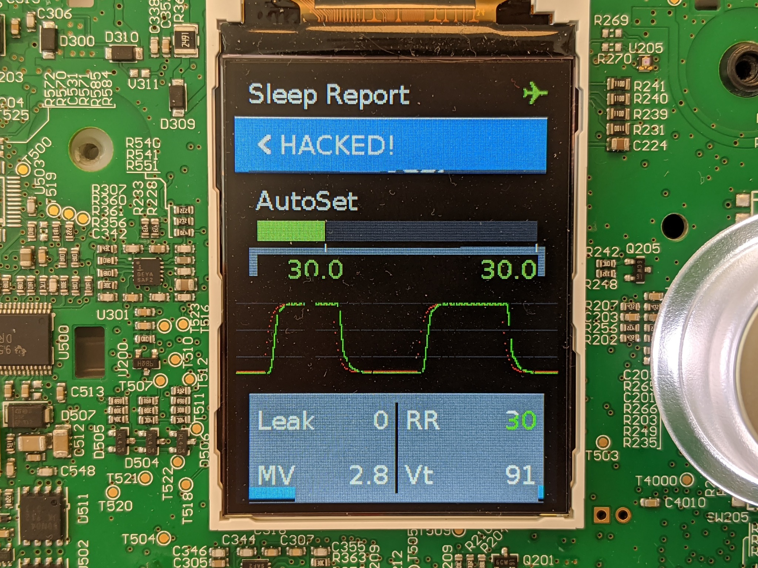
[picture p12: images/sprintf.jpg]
on the screen


# Writing extensions

There are currently two example extensions: [`breath.c`](https://github.com/osresearch/airbreak/blob/master/breath.c) and [`graph.c`](https://github.com/osresearch/airbreak/blob/master/graph.c).
The breathing mod implements a Pressure Control Ventilator with programmable
pressure and respiration rate.  The graphing mod adds a strip chart for the
current commanded pressure and the actual output pressure.

This is similar to [Magic Lantern](https://magiclantern.fm), since we use the
existing vendor firmware as a library with functions at fixed addresses and fit into
the empty space around the flash image.  The Ghidra XML file can be converted into
the `stubs.S` that provides labels at the fixed locations.

More documentation needs to be written.

Ghidra files.

Data structures.

Configuration and variables.

GUI library is based on the closed
source emwin, although [the reference manual is
available](https://www.nxp.com/docs/en/user-guide/UM03001_emWin5_5.pdf)
and can be used to derive the headers and structures required to interface
with the library.

GPIO library is the STM32 Standard Peripheral Library.

There is a hard-float unit in the CPU, but some float/double ops seem
to cause a fault.  Be sure that all of your constants have an explicit
float type like `0.1f`, otherwise gcc will use doubles.

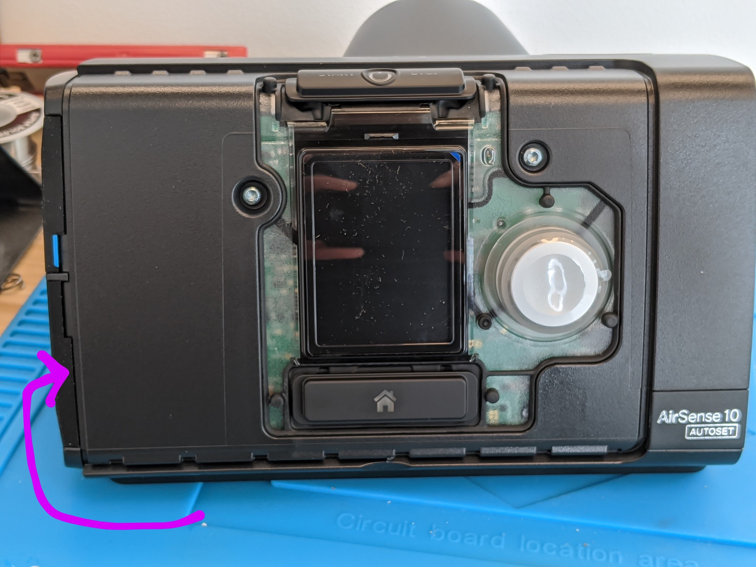
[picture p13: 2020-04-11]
docs/images/airsense-sidecover.jpg

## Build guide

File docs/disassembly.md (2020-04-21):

# Disassembly

CPAP running custom firmware

In order to dump and replace the device firmware, we need to access the programming port. Unfortunately it is inside the machine so it requires some disassembly to reach.

### Tools

You will need the following:

* Torx T10
* [ST-Link/V2 STM32 programmer](https://www.digikey.com/product-detail/en/stmicroelectronics/ST-LINK-V2/497-10484-ND/2214535) or clone
* [TC2050-IDC](https://www.digikey.com/product-detail/en/TC2050-IDC/TC2050-IDC-ND/2605366) or [TC2050-ICD-NL](https://www.digikey.com/product-detail/en/tag-connect-llc/TC2050-IDC-NL/TC2050-IDC-NL-ND/2605367) programming adapter
* 4 male-female 0.1" jumpers
* Computer with [OpenOCD](http://openocd.org/) and some Unix familiarity
* `arm-none-eabi-gcc` to compile extensions (not necessary to unlock the device)

It is difficult but possible to solder directly to the PCB, which relaxes the requirement for the jumpers and programming adapter. For more information on this, see the [list of useful test points](info/testpoints.md).

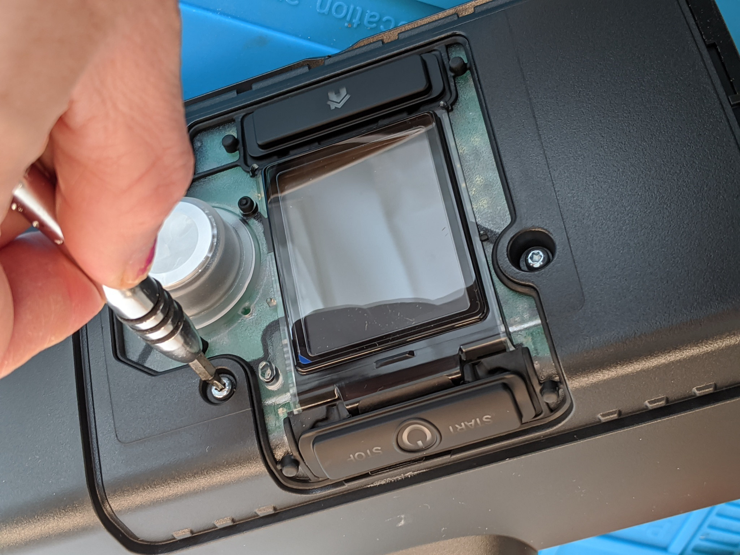
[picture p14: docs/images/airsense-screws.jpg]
Torx T10 screws


First you'll need a Torx T10 driver to remove unscrew the four faceplate screws.

<!-- ![Removing the side cover](images/airsense-sidecover.jpg) -->

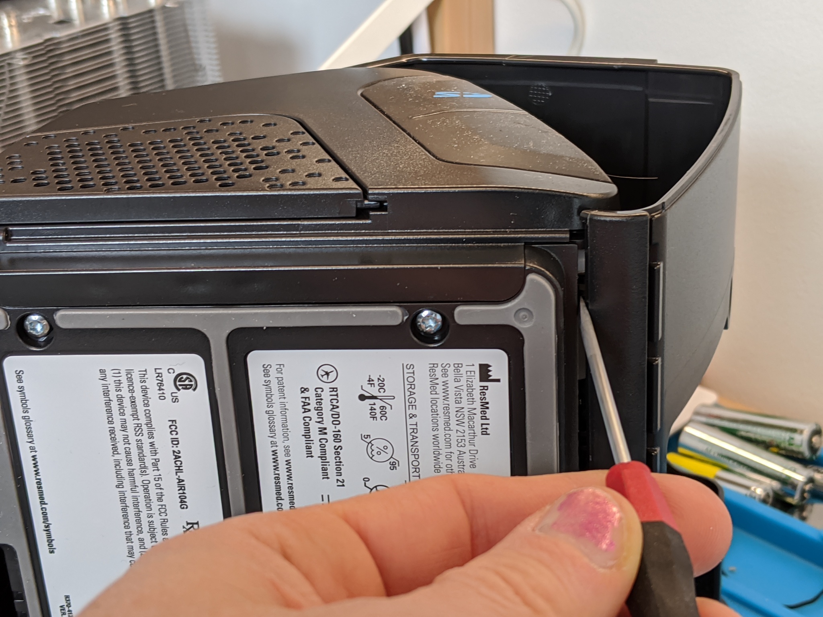
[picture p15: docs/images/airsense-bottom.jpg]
Prying the bottom latches


The bottom latches need to be pried open with a flat head or a spudger.

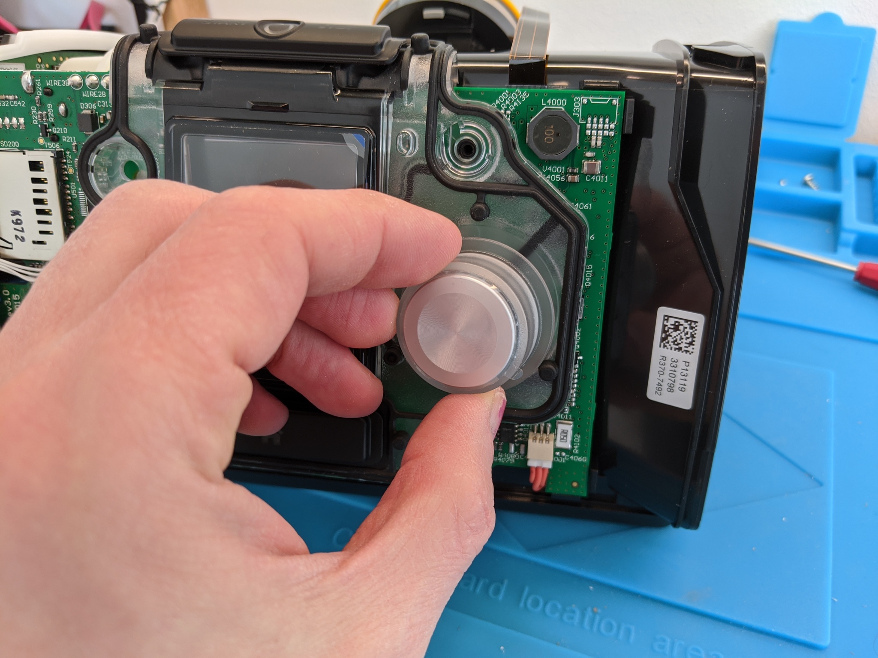
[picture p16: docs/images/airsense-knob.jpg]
Removing the knob


The knob needs to be pulled firmly straight away from the board to remove it, which will allow
the gasket to be removed.  This can be done from the front-side by popping the latches at the bottom (which are accessible), then squeezing the two latches inward on the left and right-side of the gasket around the middle.  Be careful while popping it off the start button on the top of the device (see components list for the part number if replacement needed).
It is not necessary to remove the circuit board from the device.

## Wiring

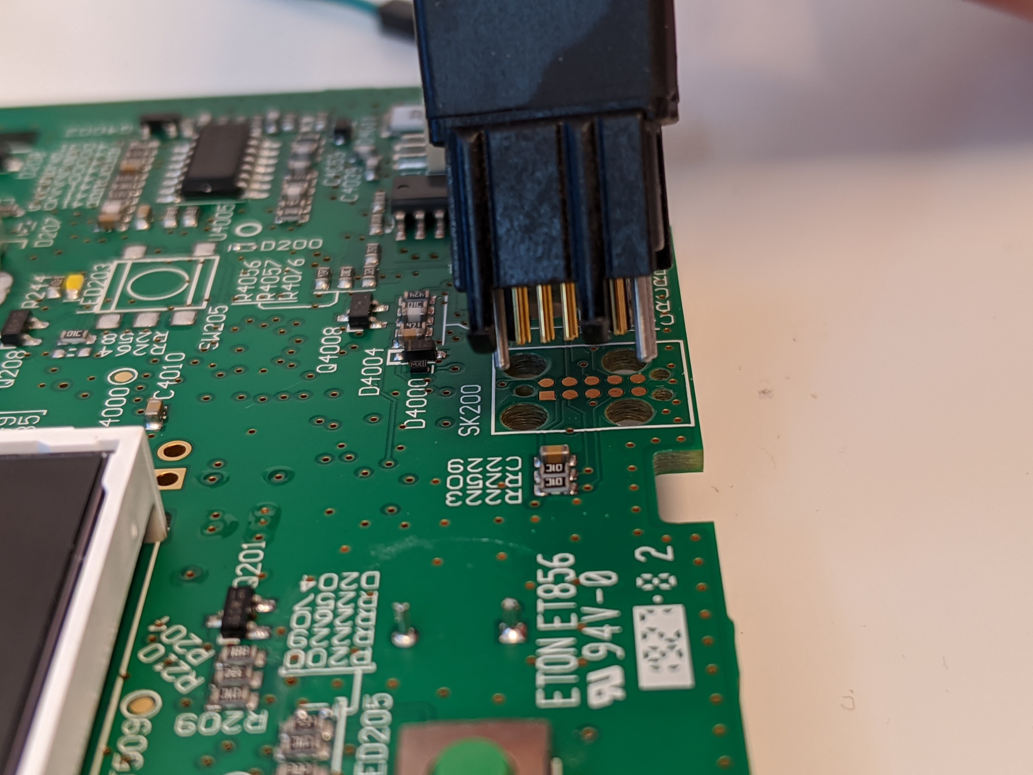
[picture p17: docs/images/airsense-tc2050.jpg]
Attaching the TC-2050 connector


[TC2050-IDC](https://www.digikey.com/product-detail/en/TC2050-IDC/TC2050-IDC-ND/2605366)
is useful for development since it has legs
that attach to the board.  For higher throughput flashing the
[TC2050-ICD-NL](https://www.digikey.com/product-detail/en/tag-connect-llc/TC2050-IDC-NL/TC2050-IDC-NL-ND/2605367)
is easier to hookup, but requires someone to hold it in place while the
device is reflashed with custom firmware.  The pinout of this port is not
the usual 10-pin ARM debug header; it combines the programming pins for
the STM32 that is the main controller, the auxiliary STM8, and the power watchdog IC.

Board footprint layout (you don't need this unless you're soldering to
the board):

| Function 		| Pin | Pin | Function |
| ---			| --- | --- | --- |
| `STM32_VDD`		| 1 (square) | 10 | `STM32_NRST` |
| `STM32_SWDIO/PMIC_TMS`| 2   | 9   | `STM8_SWIM` |
| `STM8_VDD`		| 3   | 8   | `PMIC_TDI` |
| `STM32_SWCLK/PMIC_TCK`| 4   | 7   | `STM8_NRST` |
| `GND`			| 5   | 6  | `PMIC_TDO` |

NOTE1: This follows the TC2050 pinout scheme, which is similar to "IC" pinouts (down one side, up the other).

NOTE2: The PMIC also shares some of the data pins.

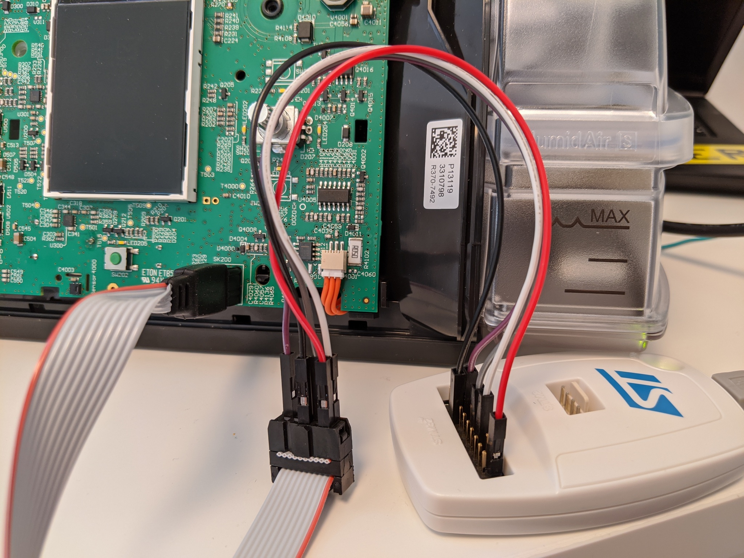
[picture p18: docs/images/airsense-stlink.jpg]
Connecting the TC-2050 to the STlink2


The [ST-Link/V2 programming
device](https://www.digikey.nl/product-detail/en/stmicroelectronics/ST-LINK-V2/497-10484-ND/2214535)
is used for flashing and debugging the code on the STM32.  It has a
different pinout from the TC2050 cable, so it is necessary to use some
male-female 0.1" jumpers to connect the four STM32 programming pins on the
TC2050 to the STlink.

TC2050 ribbon cable pinout:

| Function 		| Pin | Pin | Function |
| ---			| --- | --- | --- |
| **`STM32_VDD`**	| 1 (red) | 2 | **`STM32_SWDIO`** |
| `STM8_VDD`		| 3   | 4   | **`STM32_SWCLK`** |
| **`GND`**		| 5   | 6  | `PMIC_TDO` |
| `STM8_NRST`		| 7   | 8   | `PMIC_TDI` |
| `STM8_SWIM`		| 9   | 10   | **`STM32_NRST`** |

STlink-V2 pinout:

| Function	 	| Pin | Pin | Function |
| ---			| --- | --- | --- |
| **`STM32_VDD`**	|  1  |  2  | NC |
| NC			|  3  |  4  | NC |
| NC			|  5  |  6  | NC |
| **`STM32_SWDIO`**	|  7  |  8  | NC |
| **`STM32_SWCLK`**	|  9  | 10  | NC |
| NC			| 11  | 12  | NC |
| NC			| 13  | 14  | NC |
| **`STM32_NRST`**	| 15  | 16  | NC |
| NC			| 17  | 18  | NC |
| NC			| 19  | 20  | **`GND`** |

!!! Warning
	A genuine ST-Link programmer uses the STM32_VDD pin to detect the target voltage, not to provide power. Connecting a generic programmer or a Raspberry Pi with this pin configuration will cause the programmer to be back-powered through the AirSense PCB.

	**If you are using a SWD programmer other than a genuine ST-Link, do not hook up STM32_VDD to your 3.3V pin or you may risk damaging your board, programmer, or both!**

The following image shows the connections with the typcal low-cost ST-Link (note no VCC!).
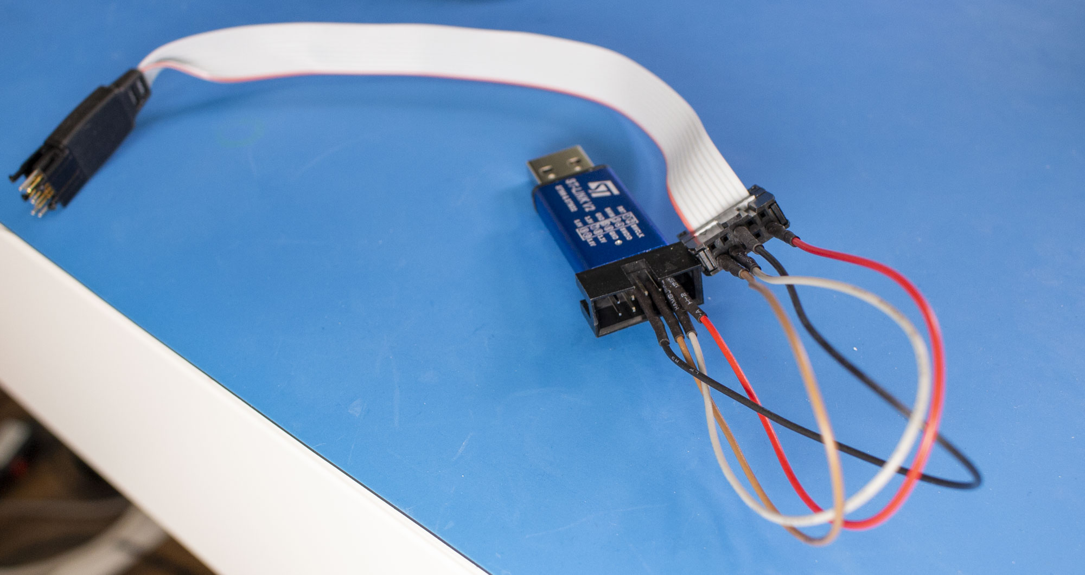
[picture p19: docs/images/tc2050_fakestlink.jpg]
Connect the TC-2050 to a Fake STLink2


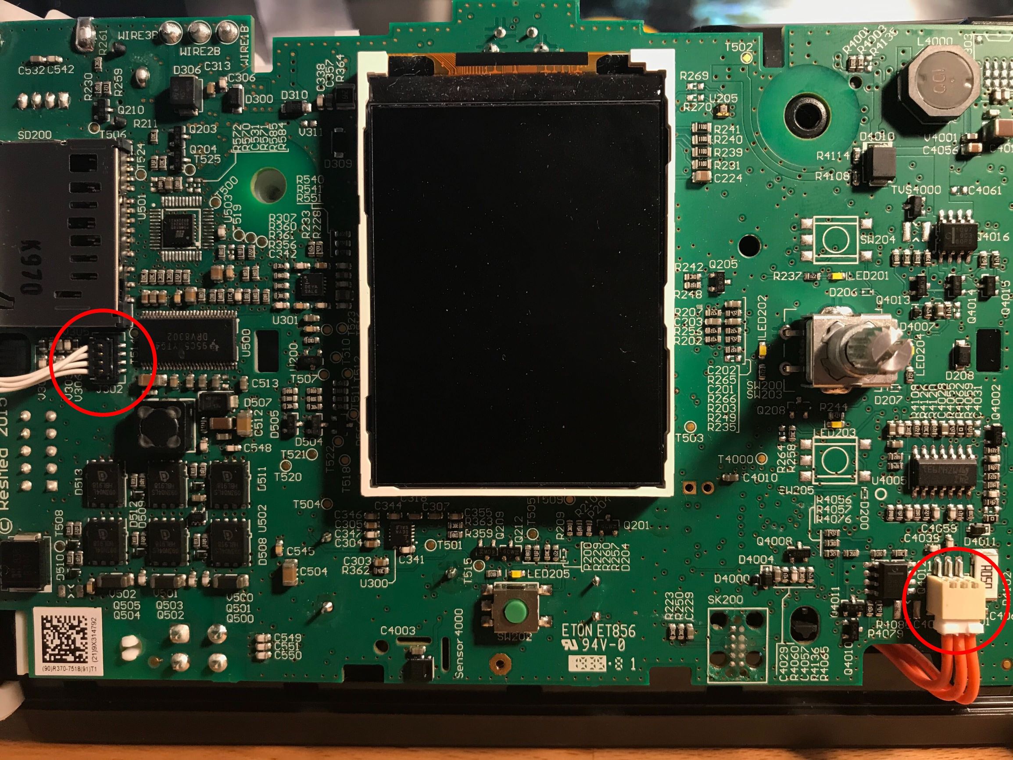
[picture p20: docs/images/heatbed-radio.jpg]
Radio and heater connections


Finally, you may wish to disconnect the cellular daughterboard (circled, left) and
humidifier (circled, right) so that the device does not 'phone home' or attempt
to heat an empty water tank.

Okay, now you're ready to [flash the firmware!](firmware.md)

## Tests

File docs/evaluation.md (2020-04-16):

# Laboratory Evaluation

<!--
To be written.  Currently the modified firmware is being evaluated by
research labs and pulmnologists.  There are other pieces necessary to
use the devices in a clinical setting, such as virus filters, O2 inputs,
remote access consoles, alarms, etc.

provide a roadmap for how these modified CPAP devices could be used.

The UK's [Rapidly Manufactured Ventilator Standards](https://docs.google.com/spreadsheets/d/17EJ9TN6O1wqP4c-lIn5hbmuMRrto7M_KXHf17zjNSLk/edit#gid=704151435)
have criteria that should be met before this sort of modification can be deployed.

Does running the pump at 30 cm H<sub>2</sub>O cause a reduction in the
life of the machine?
-->

## Setup

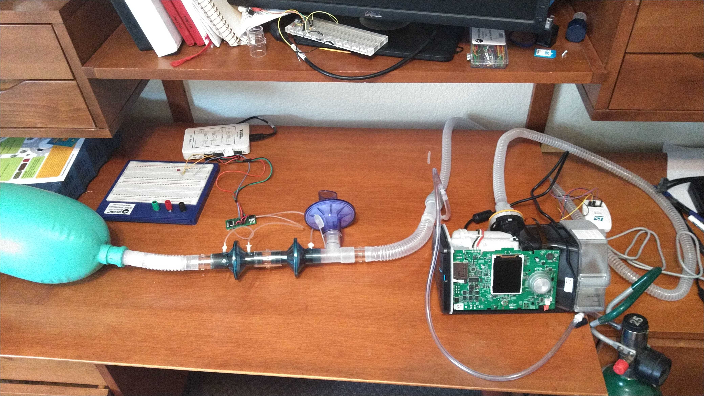
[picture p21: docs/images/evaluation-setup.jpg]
Figure 1: Experimental setup


The firmware release was flashed onto the unit and run through a
series of tests over the course of 3 days.  Maximum pressure, minimum
pressure, time at high pressure and time at low pressure were adjusted
and measurements made for a subset of the test conditions outlined in
[table 201.105 of ISO standard 80601-2-12](https://standard.no/Global/PDF/Koronakrisen%20tilgjengelig%20kostnadsfritt%202020/ISO80601-2-12_2020.pdf#page=44 "Particular requirements for basic safety and essential performance of critical care ventilators.").
A 3L bag designed to emulate the lung was salvaged from a consumables
kit used on an anesthesia machine.  The patient circuit was constructed
in accordance with the
[Mt. Sinai protocol to include a high resistance expiratory port and supplemental oxygen](https://health.mountsinai.org/wp-content/uploads/sites/14/2020/04/NIV-to-Ventilator-Modification-Protocol-v1.02-for-posting.pdf).
Air flow rate and pressure
were measured using Honeywell pressure chips and a National Instruments
data acquisition board.  Pressure was sent through a low pass filter and
calibrated using a standardized, adjustable pressure column at 0, 15.0
and 30.0 cm H<sub>2</sub>O.  Flow waveforms were acquired as a differential pressure
and calibrated using standard 0.6, 1 and 3 L syringes and integrated to
calculate tidal volumes using MATLAB.  A tube was filled with polymeric
stuffing until physiologic resistance was achieved.  Resistance and
compliance were calculated from the measured pressure volume loop.
Resistance was measured to be around 13.4 cm H<sub>2</sub>O/L/s and compliance was
measured to be 35.7 ml/cm H<sub>2</sub>O.   The test set-up is pictured in figure 1.

## Results

Figure 2: PV curves

A few test cases are presented to illustrate the high end of the
performance range.  The unit was set to a maximum pressure of 30 cm H<sub>2</sub>O, a
minimum pressure of 4 cm H<sub>2</sub>O, high pressure time of 1 second (inspiration)
and low pressure time of 2 seconds (expiration).  Results are plotted in figure 2.
Tidal volumes were calculated to be 629 ± 0.80 mL.  The system took
approximately 5 minutes to equilibrate and held stable for > 24 hours.
Peak pressures were centered around the set point of 30 cm H<sub>2</sub>O with a
range of approximately 29-32 cm H<sub>2</sub>O while minimum pressures were also
centered around the setpoint of 5 cm H<sub>2</sub>O with a range of approximately 4-6
cm H<sub>2</sub>O.  Supplemental oxygen was then supplied at a rates of 10, 15 and
20 liters per minute.  Linear increases in tidal volume were observed.
At 15 L/min of oxygen, the tidal volume increased by approximately 20 mL.  

Next steps in validation are to compare time series data from the unit
with measured values.  These tests were done anecdotally but should be
further characterized.  Pressures measured experimentally aligned well
with those reported by the unit.  Flow (tidal volume) measurements made
experimentally appear to be higher than those reported by the unit.
This could be expected due to measurement error along with the patient
circuit between the unit’s flow sensor and the experimental transducers.
Initial data indicated tidal volumes at the test lung are approximately
20% higher than those reported by the unit.  Further investigation and
characterization is warranted.

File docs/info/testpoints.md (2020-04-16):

# Useful Test Points

The Airsense S10 mainboard is covered in test points. Here are some
that may be of interest.

|  Pin | Description |
| --- | --- |
| <span style="color:#ff0000">STM32_3V3</span> | Core voltage for main uC. |
| GND | Ground. |
| <span style="color:#0000ff">SWDIO</span> | Used to program and debug main uC. |
| <span style="color:#656565">SWCLK</span> | Used to program and debug main uC. |
| <span style="color:#4f0099">SWO</span> | Could potentially be used to get further debug output from main uC (TBD). |
| <span style="color:#ff7f00">STM32_NRST</span> | Reset pin for main uC. |
| <span style="color:#66ff66">PSENSOR</span> | Scope this to get an analog pressure readout without external equipment. |
| <span style="color:#00ffff">STM8_UART</span> | UART_TX from STM8 aux uC to main uC |
| <span style="color:#663300">STM8_3V3</span> | Core voltage for aux uC |
| <span style="color:#ff00ff">STM8_SWIM</span> | Single-wire programming and debug pin for aux uC |

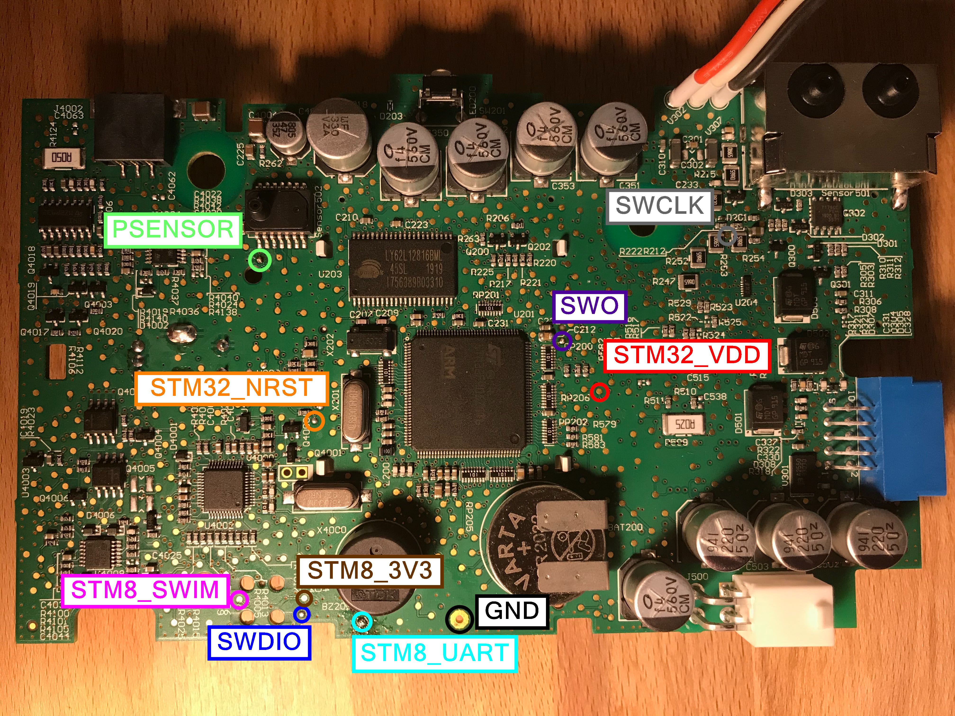
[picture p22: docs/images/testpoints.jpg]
Photo of test points on the Airsense PCB (https://airbreak.dev/images/testpoints.jpg)


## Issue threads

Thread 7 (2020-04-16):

osresearch/airbreak #7: AirStart 10 support

osresearch, 2020-04-16:
Several people have asked about the very low end AirStart 10 support.  I don't have access to one to verify compatibility, but opening this issue for tracking it.

andrewleech, 2020-04-16:
The airstart does not appear to have the control dial on the front which is going to be a limiting factor for usage
https://www.resmed.com/ap/en/consumer/products/devices/airstart-10-cpap.html
Perhaps it's the same circuit board just needing a suitable encoder soldered on, but that's unlikely to be the only difference.

I'm quite interested in support for the airsense elite, it visually looks the same at least.

osresearch, 2020-04-16:
[image]
The AirSense 10 board has two unpopulated switches (SW204 and SW205) that appear to line up with where the AirStart 10 buttons are. My guess (and this is totally a guess!) is that they are the same mainboard with different interface elements.

dakotaKat, 2020-04-16:
Working on getting a prescription updated so I can get an AirStart shipped out to me so I can tear it down and dump the flash.

colinoflynn, 2020-04-16:
@andrewleech do you mean AirSense 10 Elite? There's nothing to suggest there is any difference in HW between the "AirXXXX 10 YYYYY" units at all. I.E., the AirCurve 10 VAuto uses exact same PCB PN as the AirSense 10 CPAP if devices are of same vintage - even devices across large time-spans look to be binary compatible although PCB rev changes.

andrewleech, 2020-04-16:
@colinoflynn yes the airsense elite units are a bit cheaper than the autoset so it'd be a decent candidate. If anyone else tries it, it'd be good to confirm its not missing some of the air flow sensors etc.

colinoflynn, 2020-04-16:
Haven't looked at that specific unit, but I'd note that it's also on the list of labels (see https://fccid.io/2ACHL-AIR10CD/Label/label-info-2328354) under the FCC approval.

alanarthur, 2020-04-21:
I'd be very interested in testing to see if I can 'upgrade' my Airsense 10 Elite to become an Airsense 10 Autoset by replacing the firmware. I.e change it from being a fixed pressure machine to an automatic pressure machine

nimamoslemy, 2020-05-03:
Hi, we are a team that needs your feedback to complete our idea.
Please visit our pages and comment on it. 
[github](https://github.com/nimamoslemy/ventilator)
[gitlab](https://gitlab.com/nimamoslemy/avp-ventilator)

ArthurMafra, 2022-03-13:
> Working on getting a prescription updated so I can get an AirStart shipped out to me so I can tear it down and dump the flash.

Hi @dakotaKat , it has been long time that the project has been abandoned. Do you happen to have any Aircurve OEM firmware that I can used to fix Airsense that have been donated to me? If so I really appreciate. Best regards, arthur iphone @ gmail .com

macka-the, 2024-06-23:
Can confirm the Airsense 10 Elite is fully functional as Autoset, ASV and vAuto am currently looking for mainboard from an AirCurve 10 ST-A

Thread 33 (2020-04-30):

osresearch/airbreak #33: computed checksum did NOT match

nbritton, 2020-04-30:
root@ubuntu:~/airbreak# ./patch-airsense stm32.bin stm32-unlocked.bin
stm32.bin: FAILED
sha256sum: WARNING: 1 computed checksum did NOT match
stm32.bin: wrong hash

SW firmware version on my device is SX567-0306, it's been unplugged for about six months so I guess it did not receive the over the air updates to version SX567-0401. I don't know how to trigger the OTA firmware update process, I don't have a DME provider so I'm not even sure this unit can receive the update. The machine has one bar on the modem signal status. Is there a way to download the stock firmware update version SX567-0401 on the Internet?

nbritton, 2020-04-30:
I changed the sha256 checksum in the bash script to match my v306 firmware and flashed the device anyways. The flash appears to have worked because my machine now says "HACKED!". However, none of the extra options show up in the mode menu, it just shows CPAP and Autoset.

nbritton, 2020-04-30:
I flashed the machine back to the stock firmware, that appears to have worked as expected... the machine no longer says "HACKED!". I reset the Redmed machine with a power cycle. However, I now get this message on the Raspberry Pi... 

root@ubuntu:~/airbreak# openocd -f ./tcl/airsense.cfg
Open On-Chip Debugger 0.10.0
Licensed under GNU GPL v2
For bug reports, read
	http://openocd.org/doc/doxygen/bugs.html
BCM2835 GPIO nums: swclk = 25, swdio = 24
BCM2835 GPIO config: srst = 18
srst_only separate srst_gates_jtag srst_push_pull connect_deassert_srst
adapter speed: 2000 kHz
adapter_nsrst_delay: 100
srst_only separate srst_nogate srst_push_pull connect_deassert_srst
cortex_m reset_config sysresetreq
Info : replaced existing 'mrw' usage
Info : replaced existing 'mrw' help
Info : replaced existing 'mrb' usage
Info : replaced existing 'mrb' help
Info : replaced existing 'mmw' usage
Info : replaced existing 'mmw' help
Info : BCM2835 GPIO JTAG/SWD bitbang driver
Info : SWD only mode enabled (specify tck, tms, tdi and tdo gpios to add JTAG mode)
Info : clock speed 2002 kHz
in procedure 'init' called at file "./tcl/airsense.cfg", line 77
in procedure 'ocd_bouncer'

nbritton, 2020-04-30:
root@ubuntu:~/airbreak# openocd -f ./tcl/airsense.cfg -d 3
Open On-Chip Debugger 0.10.0
Licensed under GNU GPL v2
For bug reports, read
	http://openocd.org/doc/doxygen/bugs.html
User : 13 5 command.c:544 command_print(): debug_level: 3
Debug: 14 6 options.c:181 add_default_dirs(): bindir=/usr/bin
Debug: 15 6 options.c:182 add_default_dirs(): pkgdatadir=/usr/share/openocd
Debug: 16 6 options.c:183 add_default_dirs(): exepath=/usr/bin
Debug: 17 6 options.c:184 add_default_dirs(): bin2data=../share/openocd
Debug: 18 6 configuration.c:42 add_script_search_dir(): adding /root/.openocd
Debug: 19 6 configuration.c:42 add_script_search_dir(): adding /usr/bin/../share/openocd/site
Debug: 20 6 configuration.c:42 add_script_search_dir(): adding /usr/bin/../share/openocd/scripts
Debug: 21 6 configuration.c:82 find_file(): found ./tcl/airsense.cfg
Debug: 22 6 configuration.c:82 find_file(): found /usr/bin/../share/openocd/scripts/interface/raspberrypi2-native.cfg
Debug: 23 6 command.c:143 script_debug(): command - ocd_command ocd_command type ocd_interface bcm2835gpio
Debug: 24 7 command.c:143 script_debug(): command - interface ocd_interface bcm2835gpio
Debug: 26 7 command.c:364 register_command_handler(): registering 'ocd_bcm2835gpio_jtag_nums'...
Debug: 27 7 command.c:319 command_new(): BUG: command 'bcm2835gpio_tck_num' does not have the '.usage' field filled out
Debug: 28 7 command.c:364 register_command_handler(): registering 'ocd_bcm2835gpio_tck_num'...
Debug: 29 7 command.c:319 command_new(): BUG: command 'bcm2835gpio_tms_num' does not have the '.usage' field filled out
Debug: 30 7 command.c:364 register_command_handler(): registering 'ocd_bcm2835gpio_tms_num'...
Debug: 31 7 command.c:319 command_new(): BUG: command 'bcm2835gpio_tdo_num' does not have the '.usage' field filled out
Debug: 32 7 command.c:364 register_command_handler(): registering 'ocd_bcm2835gpio_tdo_num'...
Debug: 33 7 command.c:319 command_new(): BUG: command 'bcm2835gpio_tdi_num' does not have the '.usage' field filled out
Debug: 34 7 command.c:364 register_command_handler(): registering 'ocd_bcm2835gpio_tdi_num'...
Debug: 35 7 command.c:364 register_command_handler(): registering 'ocd_bcm2835gpio_swd_nums'...
Debug: 36 7 command.c:319 command_new(): BUG: command 'bcm2835gpio_swclk_num' does not have the '.usage' field filled out
Debug: 37 7 command.c:364 register_command_handler(): registering 'ocd_bcm2835gpio_swclk_num'...
Debug: 38 7 command.c:319 command_new(): BUG: command 'bcm2835gpio_swdio_num' does not have the '.usage' field filled out
Debug: 39 7 command.c:364 register_command_handler(): registering 'ocd_bcm2835gpio_swdio_num'...
Debug: 40 7 command.c:319 command_new(): BUG: command 'bcm2835gpio_srst_num' does not have the '.usage' field filled out
Debug: 41 7 command.c:364 register_command_handler(): registering 'ocd_bcm2835gpio_srst_num'...
Debug: 42 7 command.c:319 command_new(): BUG: command 'bcm2835gpio_trst_num' does not have the '.usage' field filled out
Debug: 43 7 command.c:364 register_command_handler(): registering 'ocd_bcm2835gpio_trst_num'...
Debug: 44 7 command.c:319 command_new(): BUG: command 'bcm2835gpio_speed_coeffs' does not have the '.usage' field filled out
Debug: 45 7 command.c:364 register_command_handler(): registering 'ocd_bcm2835gpio_speed_coeffs'...
Debug: 46 7 command.c:319 command_new(): BUG: command 'bcm2835gpio_peripheral_base' does not have the '.usage' field filled out
Debug: 47 7 command.c:364 register_command_handler(): registering 'ocd_bcm2835gpio_peripheral_base'...
Debug: 48 7 command.c:143 script_debug(): command - ocd_command ocd_command type ocd_bcm2835gpio_peripheral_base 0x3F000000
Debug: 49 8 command.c:143 script_debug(): command - bcm2835gpio_peripheral_base ocd_bcm2835gpio_peripheral_base 0x3F000000
Debug: 51 8 command.c:143 script_debug(): command - ocd_command ocd_command type ocd_bcm2835gpio_speed_coeffs 146203 36
Debug: 52 8 command.c:143 script_debug(): command - bcm2835gpio_speed_coeffs ocd_bcm2835gpio_speed_coeffs 146203 36
Debug: 54 8 command.c:143 script_debug(): command - ocd_command ocd_command type ocd_bcm2835gpio_swd_nums 25 24
Debug: 55 8 command.c:143 script_debug(): command - bcm2835gpio_swd_nums ocd_bcm2835gpio_swd_nums 25 24
User : 57 8 command.c:544 command_print(): BCM2835 GPIO nums: swclk = 25, swdio = 24
Debug: 58 8 command.c:143 script_debug(): command - ocd_command ocd_command type ocd_bcm2835gpio_srst_num 18
Debug: 59 8 command.c:143 script_debug(): command - bcm2835gpio_srst_num ocd_bcm2835gpio_srst_num 18
User : 61 8 command.c:544 command_print(): BCM2835 GPIO config: srst = 18
Debug: 62 8 command.c:143 script_debug(): command - ocd_command ocd_command type ocd_reset_config srst_only srst_push_pull
Debug: 63 8 command.c:143 script_debug(): command - reset_config ocd_reset_config srst_only srst_push_pull
User : 65 8 command.c:544 command_print(): srst_only separate srst_gates_jtag srst_push_pull connect_deassert_srst
Debug: 66 8 command.c:143 script_debug(): command - ocd_command ocd_command type ocd_transport select swd
Debug: 67 8 command.c:143 script_debug(): command - ocd_transport ocd_transport select swd
Debug: 68 8 command.c:319 command_new(): BUG: command 'swd' does not have the '.usage' field filled out
Debug: 69 8 command.c:364 register_command_handler(): registering 'ocd_swd'...
Debug: 70 8 bitbang.c:353 bitbang_swd_init(): bitbang_swd_init
[... cut ...]
Debug: 307 22 bitbang.c:531 bitbang_swd_run_queue(): bitbang_swd_run_queue
Debug: 308 22 bitbang.c:360 bitbang_exchange(): bitbang_exchange
Debug: 309 22 bitbang.c:538 bitbang_swd_run_queue(): SWD queue return value: 07
Debug: 310 22 command.c:626 run_command(): Command failed with error code 7
User : 311 22 command.c:687 command_run_line(): in procedure 'init' called at file "./tcl/airsense.cfg", line 78
in procedure 'ocd_bouncer'
Debug: 312 22 command.c:626 run_command(): Command failed with error code -4
User : 313 23 command.c:687 command_run_line():

nbritton, 2020-04-30:
I very briefly had it working after I shorted RST to v3.3 (R-Pi pin 1)... the following was output to the terminal... I'm wondering if maybe I have a loose wiring? I soldered them to the board and they seem solidly attached to the pads. However, when I wiggle SWDIO and restart openocd it sometimes briefly works (gets to the dump message). I'm struggling to isolate the wire or figure out a pattern to help me troubleshoot. I didn't find any issues yet with a multimeter continuity test. I guess I'll try desoldering the connection tomorrow.

root@ubuntu:~/airbreak# openocd -f ./tcl/airsense.cfg
Open On-Chip Debugger 0.10.0
Licensed under GNU GPL v2
For bug reports, read
	http://openocd.org/doc/doxygen/bugs.html
BCM2835 GPIO nums: swclk = 25, swdio = 24
BCM2835 GPIO config: srst = 18
srst_only separate srst_gates_jtag srst_push_pull connect_deassert_srst
adapter speed: 2000 kHz
adapter_nsrst_delay: 100
srst_only separate srst_nogate srst_push_pull connect_deassert_srst
cortex_m reset_config sysresetreq
Info : replaced existing 'mrw' usage
Info : replaced existing 'mrw' help
Info : replaced existing 'mrb' usage
Info : replaced existing 'mrb' help
Info : replaced existing 'mmw' usage
Info : replaced existing 'mmw' help
Info : BCM2835 GPIO JTAG/SWD bitbang driver
Info : SWD only mode enabled (specify tck, tms, tdi and tdo gpios to add JTAG mode)
Info : clock speed 2002 kHz
Info : SWD DPIDR 0x2ba01477
Info : stm32f4x.cpu: hardware has 6 breakpoints, 4 watchpoints
This device is not running modified firmware.
File stm32.bin not found!
Backup of stock firmware image not found.
Please type 'dump' to save the stock firmware to disk.

Polling target stm32f4x.cpu failed, trying to reexamine
Error: Could not initialize the debug port
Examination failed, GDB will be halted. Polling again in 100ms
Polling target stm32f4x.cpu failed, trying to reexamine
Error: Could not initialize the debug port
Examination failed, GDB will be halted. Polling again in 300ms
Polling target stm32f4x.cpu failed, trying to reexamine
Error: Could not initialize the debug port
Examination failed, GDB will be halted. Polling again in 700ms
Polling target stm32f4x.cpu failed, trying to reexamine
Error: Could not initialize the debug port
Examination failed, GDB will be halted. Polling again in 1500ms
Polling target stm32f4x.cpu failed, trying to reexamine
Error: Could not initialize the debug port
Examination failed, GDB will be halted. Polling again in 3100ms
Polling target stm32f4x.cpu failed, trying to reexamine
Error: Could not initialize the debug port
Examination failed, GDB will be halted. Polling again in 6300ms
Polling target stm32f4x.cpu failed, trying to reexamine
Error: Could not initialize the debug port
Examination failed, GDB will be halted. Polling again in 6300ms
Polling target stm32f4x.cpu failed, trying to reexamine
Error: Could not initialize the debug port
Examination failed, GDB will be halted. Polling again in 6300ms
Polling target stm32f4x.cpu failed, trying to reexamine
Error: Could not initialize the debug port
Examination failed, GDB will be halted. Polling again in 6300ms
^C

dblunk88, 2020-04-30:
Just a FYI: I'm running into the same checksum mismatch and I have the same checksum as you

dblunk88, 2020-04-30:
Hash is equivalent to SW version: SX567-0306

nbritton, 2020-04-30:
Good news, it turns out it was a bad connection on the SWDIO wire, I desoldered the old wire and cleaned up the pad and soldered on an entirely new wire. Now openocd is working as expected on the very first attempt. The old wire didn't fail continuity testing, but I think the problem was the wire just had very high resistance relatively speaking that was degrading the digital signaling... the pad is so small and maybe the rosin core I used was interfering with the little bit of contact surface... I don't know, but openocd is working now!

Now I just need to figure out how to injects the rights bits in the right places with the v306 firmware that I have, but ideally I would like to figure out how to upgrade my machine to v401.

dblunk88, 2020-04-30:
Is there a reason why we aren't sharing the firmware dumps? This would make it a lot easier for people who haven't been getting OTA updates

colinoflynn, 2020-04-30:
The firmware is copyright material, and should **never** be shared (or even links to such material submitted). People doing so would jeopardize the entire project.

Note that the same SW version number encompasses a large group of potentially incompatible firmware as as well. The firmware (and location of stuff) changes also with the 'catalog no' on the back. It's possible some catalog no's are never OTA to the latest FW version as well, which could be due to compatibility reasons for example.

dblunk88, 2020-04-30:
Aw, that makes sense! Thank you for the clarification and for all of the hard work you and others have put in to this project.

nbritton, 2020-04-30:
This is from the patch-airsense script:

extra_modes() {
        BUILD_FLAGS=$(( BUILD_FLAGS | (1 << 3) ))
        # add more mode entries, set config 0x0 mask to all bits high
        # default is 0x3, which only enables mode 1 (CPAP) and 2 (AutoSet)
        # ---> This is the real magic <---
        printf '\xff\xff' | patch 0x8590 || die failed
}

From someone who has a v401 firmware, what exactly is located at 0x8590? I'm wondering if I can use xxd and just grep for that string to find the correct location in my v306 firmware to patch. A grep for just 0303 returns too many entries.

gszakacs, 2020-04-30:
> Is there a reason why we aren't sharing the firmware dumps? This would make it a lot easier for people who haven't been getting OTA updates

It does not appear that the manufacturer is pushing updates to devices, It seems that patients need to go to their doctor to have the devices updated to newer firmware versions. 

Ref: http://www.apneaboard.com/forums/Thread-Resmed-Airsense-10-Autoset-firmware-update?page=3

dblunk88, 2020-04-30:
> This is from the patch-airsense script:
>
> extra_modes() {
> BUILD_FLAGS=$(( BUILD_FLAGS | (1 << 3) ))
> # add more mode entries, set config 0x0 mask to all bits high
> # default is 0x3, which only enables [...]

I've asked around and may have found a friend with the newer firmware who would let me borrow his device. Since I'd have access to both dumps, I could see if I can compare both

nbritton, 2020-04-30:
I have new modes now after my latest flash:

[image]

[image]

[image]

root@ubuntu:~/airbreak# git diff patch-airsense
diff --git a/patch-airsense b/patch-airsense
index b0e58d4..4b315e2 100755
--- a/patch-airsense
+++ b/patch-airsense
@@ -20,7 +20,7 @@ patch() {
        dd bs=1 seek=$offset conv=notrunc of="$OUT" status=none
 }
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

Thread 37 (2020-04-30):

osresearch/airbreak #37: Raspberry Pi HowTo

nbritton, 2020-04-30:
[image]

[image]

[image]

[image]

[image]

[image]

[image]

[image]

**Ubuntu 20.04 Raspberry Pi 3 Image Download Link:** https://ubuntu.com/download/raspberry-pi/thank-you?version=20.04&architecture=armhf+raspi

[image]

[image]

[image]

[image]

[image]

gszakacs, 2020-04-30:
Thanks to your pics, I was able to troubleshoot the issue with my hardware setup and able to dump the bin file.

dblunk88, 2020-04-30:
Is there any chance that this can be added to the wiki?

davelatt, 2020-06-11:
Hi Nikolas,

My name is Dave Lattimore and I saw you Post on the apnea boards about enabling ASV. I had the thread bookmarked but they removed the post. Guess someone didn't like the idea of an AirBreak :-). I was going to private message you to see if there are any issues with missing ASV data structures but I don't have you logon id. My "apnea board" and "cpaptalk" id is sosotired. My email is davelatt@hotmail.com.  Please get in touch.
Thanks,
Dave

amorton12, 2022-05-11:
For any future hackers that come across this and are using a RasPi B version one, like me, you’ll need to do the following:

Wire your serial clock line to the SPI0 sclk pin GPIO11, data to GPIO25, reset to GPIO24. 

Modify /usr/share/openocd/scripts/interface/raspberrypi-native.cfg 

Uncomment the two lines 
bcm2835gpio_srst_num 24
reset_config srst_only srst_push_pull

Modify the rasp-pi.cfg to source the raspberrypi-native.cfg rather than raspberrypi2-native.cfg

The rest works the same. I successfully dumped and flashed the 0306 image from both a cpap and an autoset version of the Airsense 10 with this config (and verified that they are interchangeable).

jayhathaway, 2022-08-28:
> For any future hackers that come across this and are using a RasPi B version one, like me, you’ll need to do the following:
>
> Wire your serial clock line to the SPI0 sclk pin GPIO11, data to GPIO25, [...]

Cool thanks! So did your flash with 0306 go smoothly without any issues?

ttkirst, 2022-11-20:
> > Cool thanks! So did your flash with 0306 go smoothly without any issues?
> 
> Yes, I flashed the Autoset stock image and the unlocked/modified image onto the base model CPAP machine with this. Both worked perfectly, and I've been using that machine daily in Autoset mode for about 4 months.

Hi, I am trying to airbreak my Airsense 10 CPAP elite with a raspberry pi 4 as the programmer. I follower your instructions but I cant seem to get it to work properly. It connects to the uC but won't dump the firmware and keeps giving errors. Could you please assist?

Kind regards,
Tyler

root@raspberrypi:/home/pi/airbreak# sudo openocd -f tcl/rasp-pi.cfg -f tcl/airsense.cfg
Open On-Chip Debugger 0.11.0-rc2
Licensed under GNU GPL v2
For bug reports, read
	http://openocd.org/doc/doxygen/bugs.html
0x2000
Info : replaced existing 'mrw' usage
Info : replaced existing 'mrw' help
Info : replaced existing 'mrh' usage
Info : replaced existing 'mrh' help
Info : replaced existing 'mrb' usage
Info : replaced existing 'mrb' help
Info : replaced existing 'mmw' usage
Info : replaced existing 'mmw' help
Info : BCM2835 GPIO JTAG/SWD bitbang driver
Info : clock speed 2001 kHz
Info : SWD DPIDR 0x2ba01477
Info : stm32f4x.cpu: hardware has 6 breakpoints, 4 watchpoints
Info : starting gdb server for stm32f4x.cpu on 3333
Info : Listening on port 3333 for gdb connections
This device is not running modified firmware.
File stm32.bin not found!
Backup of stock firmware image not found.
Please type 'dump' to save the stock firmware to disk.

Info : Listening on port 6666 for tcl connections
Info : Listening on port 4444 for telnet connections
Polling target stm32f4x.cpu failed, trying to reexamine
Info : SWD DPIDR 0x2ba01477
Info : SWD DPIDR 0x2ba01477
Error: Could not find MEM-AP to control the core
Examination failed, GDB will be halted. Polling again in 100ms
Info : SWD DPIDR 0x2ba01477
Polling target stm32f4x.cpu failed, trying to reexamine
Info : SWD DPIDR 0x2ba01477
Info : SWD DPIDR 0x2ba01477
Info : SWD DPIDR 0x2ba01477
Error: Could not find MEM-AP to control the core
Examination failed, GDB will be halted. Polling again in 300ms
Info : SWD DPIDR 0x2ba01477
Polling target stm32f4x.cpu failed, trying to reexamine
Info : stm32f4x.cpu: hardware has 6 breakpoints, 4 watchpoints
Polling target stm32f4x.cpu failed, trying to reexamine
Info : SWD DPIDR 0x2ba01477
Info : SWD DPIDR 0x2ba01477
Info : SWD DPIDR 0x2ba01477
Error: Could not find MEM-AP to control the core
Examination failed, GDB will be halted. Polling again in 100ms
Info : SWD DPIDR 0x2ba01477
Polling target stm32f4x.cpu failed, trying to reexamine
Info : SWD DPIDR 0x2ba01477
Info : SWD DPIDR 0x2ba01477
Error: Could not find MEM-AP to control the core
Examination failed, GDB will be halted. Polling again in 300ms
Info : SWD DPIDR 0x2ba01477
Polling target stm32f4x.cpu failed, trying to reexamine
Info : SWD DPIDR 0x2ba01477
Info : SWD DPIDR 0x2ba01477
Error: Could not find MEM-AP to control the core
Examination failed, GDB will be halted. Polling again in 700ms
Info : SWD DPIDR 0x2ba01477
Polling target stm32f4x.cpu failed, trying to reexamine
Info : SWD DPIDR 0x2ba01477
Info : SWD DPIDR 0x2ba01477
Info : SWD DPIDR 0x2ba01477
Info : SWD DPIDR 0x2ba01477
Error: Could not find MEM-AP to control the core
Examination failed, GDB will be halted. Polling again in 1500ms
Info : SWD DPIDR 0x2ba01477
Polling target stm32f4x.cpu failed, trying to reexamine
Info : stm32f4x.cpu: hardware has 6 breakpoints, 4 watchpoints
Polling target stm32f4x.cpu failed, trying to reexamine
Info : SWD DPIDR 0x2ba01477
Info : SWD DPIDR 0x2ba01477
Error: Could not find MEM-AP to control the core
Examination failed, GDB will be halted. Polling again in 100ms

ttkirst, 2022-11-20:
This is the error I get when I try dump the firmware... Please someone assist, been trying for 2 days straight...

root@raspberrypi:/home/pi/airbreak# telnet localhost 4444
Trying ::1...
Trying 127.0.0.1...
Connected to localhost.
Escape character is '^]'.
Open On-Chip Debugger
> reset halt
target halted due to debug-request, current mode: Thread 
xPSR: 0x01000000 pc: 0x0800021c msp: 0x2000f000
> dump
Dumping stm32.bin, 0x100000 bytes at 0x08000000...
SWD DPIDR 0x2ba01477
Failed to read memory and, additionally, failed to find out where

amorton12, 2022-11-20:
> 

> Hi, I am trying to airbreak my Airsense 10 CPAP elite with a raspberry pi 4 as the programmer. I follower your instructions but I cant seem to get it to work properly. It connects to the uC but [...]

Disclaimer: I am far, far from any kind of expert here. This was my first time trying to talk to any kind of STM microcontroller 

You definitely don’t want to follow my instructions with a Pi 4, but you may need to do what I did. I looked up the port/pin assignments for my version one Pi compared to the instructions that were written for a Pi 2/3, and made those adjustments so that it was using the same port functions, just on different pins. 

I would guess that the original instructions are probably closer to what you need than mine, since mine are adapted for a much earlier revision of the Pi hardware. It took me a few days of hacking at it and taking breaks before I figured it out, so you’re not the only one to struggle with it. I had actually ordered a USB programmer and it was in the mail when I finally figured it out, so worst case scenario you can throw in the towel and spend an extra $10 or so to get it done.

ttkirst, 2022-11-20:
> Disclaimer: I am far, far from any kind of expert here. This was my first time trying to talk to any kind of STM microcontroller
>
> You definitely don’t want to follow my instructions with a Pi 4, but [...]

Thanks so much for the reply, I really appreciate it.
I did basically follow the original, just made the changes to suite pi 4 as you suggested. Think the hardware is basically working since I can connect and dump some data. My issue is it won't dump all. The reason I came to your post is mainly due to the firmware difference, thought maybe that had a part to play. Mine is 0302... Was trying to figure out how you managed to patch it? I saw the attached patch file above but not sure how to use it or what file to apply the patch to? Does it replace the current airsense patch file? and use it to patch my firmware when I manage to dump it? Or...?

On a different note, this is what I get when I use dump_all, seems to fail at the same place...

> dump_all
Dumping syscfg.bin, 0x400 bytes at 0x40013800...
Dumping bkpsram.bin, 0x1000 bytes at 0x40024000...
Dumping rtc_bkpr.bin, 0x50 bytes at 0x40002850...
Dumping optionbytes.bin, 0x8 bytes at 0x1fffc000...
Dumping bank0.bin, 0x100000 bytes at 0x08000000...
SWD DPIDR 0x2ba01477
Failed to read memory and, additionally, failed to find out where

Thanks so much for your feedback, good to know its not just me struggling.

amorton12, 2022-11-20:
The dump process will be the same regardless of version - the difference comes in with the actual patching, since the key pieces of data that need to be flipped around will be at different offsets in the file - I think there’s a patch or a fork out there with a file that contains the correct offsets for your firmware, but don’t quote me on that - it’s been quite a while since I worked on this. 

I do have a Pi 400, which afaik, has the same pin out as the Pi 4, so if I have a need to take one of my machines apart, I may fire it up and take a crack at it. If I have any luck, I’ll post here again with whatever worked.

ttkirst, 2022-11-20:
> The dump process will be the same regardless of version - the difference comes in with the actual patching, since the key pieces of data that need to be flipped around will be at different offsets [...]

Cool, thanks so much. If I manage to get it working I will add details to this thread to hopefully help the next person. At the moment I’m thinking it is protection bits or something along those lines preventing me from reading that location. The error “could not find MEM-AP to control the core” is also a little concerning 🙈

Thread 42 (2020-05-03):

osresearch/airbreak #42: missing menu items in some modes

bdarcus, 2020-05-03:
Some of the modes are missing important, even critical, settings.

In particular, ST, T, PAC are missing ability to set a respiratory rate or backup rate. Without that, I'm pretty sure they're unusable.

Also, "learn targets" and "height" are missing from the iVAPs menus.

This is on a vauto.

gszakacs, 2020-05-03:
I noticed that. Either access to / editing of those menu items or perhaps the precompiled breath.bin/graph.bin would be helpful. 
In case folks are wondering what are the settings for the covid19 related ventilation support modes, you may find the following useful.
[image]
[image]
[image]
[image]

bdarcus, 2020-05-03:
> What firmware do you have ? 

-0401.

> Have you tried compiling/re-flashing with the "all_menu" function enabled ? 

No, in part because I wasn't clear what the purpose of that was. It won't help if items are grayed out.

> I agree that editing those variables may be critical for covid19 related ventiltation.

The RR and BR settings are fundamental to those modes; and yeah, likely critical for covid patients.

nbritton, 2020-05-03:
I can confirm bdarcus original post, these items are not present on my AS10v306. I'm not using the all_menu feature.

bdarcus, 2020-05-04:
So it's confirmed across different machines and fw, including the default autoset and -0401.

I assume this is straightforward to fix, but I don't understand how myself.

bdarcus, 2020-05-06:
Someone did try the all_menu option, and while it does disclose the additional necessary menu items noted here, it's not very practical, since it adds all menus, even when not relevant. We don't want that.

So somehow you need to get these specific menu items added to the standard unlocking.

nbritton, 2020-05-09:
On my AirCurve S with firmware 0306 all of the setting parameters are visible in iVAPS mode (without enabling the force all menus modification), with the exception of Height.

I have a xxd hex diff of my AirSense 10 AutoSet and AirCurve S, both have firmware version 0306. 626 memory addresses have different values between the two firmwares. I'm analyzing the differences.

nbritton, 2020-05-10:
I have good news and bad news. The good news is that the decompiled C source code that Ghidra generated are identical, this basically means that the "runtime engine" is entirely intact. Additional good new is that the hardware is also identical as near as I can tell, both my AirSense 10 AutoSet and AirCurve 10 S both have exactly the same mainboard part numbers.

The bad news, the AirCurve 10 S firmware has data structures / header definitions that are not present in the AirSense 10 AutoSet firmware. This is entirely why the missing items in your original post are missing, so if a menu item is missing that means the data structure isn't defined within the firmware. The firmware would have to be patched to add these data structures.

I did flash my AirSense with my AirCurve's firmware, this worked perfectly and all the data structure definitions that the AirCurve had are present and operational. So let me be clear, this issue is entirely a software limitation. If someone had a genuine AirCurve 10 ST-A firmware this device would have all the data structure definitions and flashing it onto virtually any other device, such as an AirSense 10 AutoSet, would enable a device that has 100% functional iVAPS and PAC modes.

The serial number and other vital product information are not stored within the firmware, that information is stored in an EEPROM; there is no uniquely identifiable information contained in the stock stm32.bin firmware file that OpenOCD dumps.

bdarcus, 2020-05-10:
Hmm ... so in those modes, one is stuck with the fixed default rates.

I imagine that might work for some patients, in some circumstances. But
definitely not ideal.

nbritton, 2020-05-10:
I'm not sure, but it might be more than that. The mode algorithm that the runtime engine is using could simply ignore the parameters that aren't defined. If that's true it would be harder to trust that the algorithm will do the right thing because we don't know how the algorithm uses the sensor and statistical data for making decisions about the flow. For instance, my AirSense didn't know how to derived and track Ti and I:E statistics until I flashed it with the firmware from my AirCurve 10 S.

[image]

[image]

bdarcus, 2020-05-10:
All height does is define a variable to calculate the target MV, which one can do manually also. Why I mentioned it's missing, but not critical.

But RR or BU on the other modes is more important, and what I was referring to when mentioning the "defaults" in my last comment. The modes do run at those default settings without the menus for them.

ruri-baka, 2020-05-11:
It ultimately has to do with how the GUI is compiled for certain sets of machines. The actual values though are still present. It should be possible to set the missing variables through the serial console (see the serial to accessory port pcb) as a workaround.

bdarcus, 2020-05-12:
> It should be possible to set the missing variables through the serial console (see the serial to accessory port pcb) as a workaround.

Probably wouldn't be practical, though, in an emergent hospital environment?

zhuhongchao, 2021-06-28:
> I'm not sure, but I think it might be more than that. The mode algorithm that the runtime engine is using could simply ignore the parameters that aren't defined. If that's true it would be harder to trust that the algorithm will do the right thing because we don't know how the algorithm uses the sensor and statistical data for making decisions about the flow generation. For instance, my AirSense didn't know how to derived and track Ti, Ti Min, Ti Max, and I:E statistics until I flashed it with the firmware from my AirCurve 10 S. In the diff comparison of the AirSense and AirCurve firmwares, the only noticeable difference was the AirCurve had these Ti and I:E data structures defined... these structures were absent in the AirSense firmware.
> 
> [GIF of iVAPS operation on AirSense with AirCurve S firmware](https://i.imgur.com/vF7Btrj.mp4)
> 
> [GIF of iVAPS operation on AirSense with AirSense firmware (all menus visible mod enabled)](https://i.imgur.com/6WdtTv1.mp4)
> 
> **Update:** I noticed in the second GIF that "Height" wasn't marked out with a --, so I tried changing the Height setting and it worked... this then implies that all the necessary data structures are present on the AirCurve 10 S to support iVAPS mode.

I have modified the AIRSENSE AUTOSET firmware according to the instructions and added some new modes, but some parameters are missing. Is it possible to give me the firmware for aircurve?

ArthurMafra, 2022-03-13:
> Some of the modes are missing important, even critical, settings.
> 
> In particular, ST, T, PAC are missing the ability to set a `"Resp. Rate"` or `"Backup Rate"`.
> 
> Without those, one can't really use those modes, which are likely the most useful ones for COVID-19 patients.
> 
> Also, `"Learn Targets"` and `"Height"` are missing from the iVAPS menus.

Hi @bdarcus, may you have Aircurve firmware for share? I have donated device that is buddy only asv auto working. I would like to flash original OEM Aircurve firmware in. If you have backup oem and are willing to help please send to arthuriphone @ gmail. com. Thank you.

jayhathaway, 2023-03-10:
Does anyone have the aircurve vauto firmware they are willing to share privately?

shaareable, 2023-03-10:
@jayhathaway I have a new vauto. You'd need to walk me through it maybe?

DocFreeman, 2023-06-25:
> I actually just got my hands on the firmware. Thank you for offering! On Fri, Mar 10, 2023 at 9:19 AM Jay Hathaway ***@***.***> wrote:
> […](#)

I'm also looking for this .bin file. Would love it if you could help me out.

jayhathaway, 2023-06-26:
https://drive.google.com/file/d/1fFEThG_DEakaaTcObgKXwwoApSy2G3RU/view?usp=drive_link

DocFreeman, 2023-07-17:
> https://drive.google.com/file/d/1fFEThG_DEakaaTcObgKXwwoApSy2G3RU/view?usp=drive_link
> […](#)

Much appreciated! I think the repo maintainers would appreciate it as well if you got rid of the link, airbreak does not distribute copyrighted files.

BravoIndia, 2024-06-14:
> I did flash my AirSense with my AirCurve's firmware, this worked perfectly and all the data structure definitions that the AirCurve had are present and operational. So let me be clear, this issue is entirely an artificial software limitation. If someone had an AirCurve 10 ST-A firmware this device would have all the data structure definitions and flashing its firmware onto virtually any other device, such as an AirSense 10 AutoSet, would enable a device that has 100% functional iVAPS and PAC modes. So if you have access to an AirCurve 10 ST-A, you can clone its firmware onto a base model AirSense or AirCurse device. In an assembly line situation, a machine can be disassembled and re-flashed with ST-A iVAPS / PAC ventilator modes in less than 10 minutes per machine per person.
> 
> The serial number and other vital product information are not stored within the firmware, that information is stored in an EEPROM; there is no uniquely identifiable information contained in the stock stm32.bin firmware file that OpenOCD dumps.

@nbritton Any chance I could contact you about your experimentation flashing AirCurve 10 S firmware onto the AirSense 10 AutoSet? Very much hoping you see this, thanks.

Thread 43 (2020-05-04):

osresearch/airbreak #43: Brazilian Portuguese firmware

quilombodigital, 2020-05-04:
Hi,

I am from Brazil and I am trying to patch a brazilian portuguese firmware.
I don't know the firmware version because it does not show it (there is no about screen)
Like everyone I first stopped at the checksum issue, my checksum is ad5486f5c4721448893bc4edcb5905ba38b034ee54f00205bfcbe075fefab8e7.

I checked some offsets from the code and they seemed to match, so I decided to give it a try.
I changed the checksum and continued, to see how far could I go and I stopped at other issue:

_make: *** No rule to make target 'stm32.bin.xml', needed by 'stubs.S'. Stop._

Installed ghidra, analyzed using 'stm32 cortex little endian' , and generated XML and used it, but I am pretty sure this is not correct, since my guess is that the symbol names should come from somewhere else, and not auto generated, probably for offset matching. Then got stucked at:

_undefined reference to 'tim_read_tim5_

Trying to advance a little more, I commented the ghidrastubs part and flashed it.
Nothing looked different, no 'hacked' message, then I tried to enable 'all_menu' and some menu items in the menu changed, but no major feature enabled. 

Original Screens:
[image]
[image]
[image]

I need some guidance about what are the correct steps to adapt my firmware. I read the github issues but I am a little confused by everything.
Do I have to look for offset matches in version 401 and change the script? (I don't have a 401 firmware, I only have mine, what now?)
What about this ghidra stuff? what I must do inside it? where the names came from?
A small tutorial saying "1-match all offsets of blah to bleh, 2-convert xxx..." 

Thank you all for this incredible project.
The Brazilian health system is very precarious, you will be saving many lives.

dblunk88, 2020-05-04:
So, for the firmware, press the big round button and the bottom botton for a few seconds. This will take you to the clinical menu, where you can check your firmware version. Technically you do not need to compile to run it, just run the patcher and patch in the firmware... but there is a problem. You're running on neither 401 'nor 306 if that is your checksum... so you might have to find the offsets yourself.

tim5, from my understanding, calculates the current system time and if I recall correctly, there may even be the offset number (for 401) in the source... might be worth trying to rename the function in the XML (then again, I may be wrong).

gszakacs, 2020-05-04:
Finding it in the clinical menu is the easiest. I think you could also find it in the binary file at address 0x00040000.
[image]

dblunk88, 2020-05-04:
Oh nice. The patcher might work, change the checksum and give it a try. If you're compiling, give mine a shot:

https://github.com/dblunk88/airbreak/blob/master/patch-airsense

quilombodigital, 2020-05-04:
Hi,
The version is 306, so I used your script and it went normally. thank you!

Everything seems to have worked, and the modes are available, but when I choose ST or iVaps, It begins the screen, give a small blow, and then it restarts the everything and keeps restarting the machine. 

Any idea? Am I missing something?

[image]

gszakacs, 2020-05-04:
I have the 306 and the ivap mode works with a limited feature set on my 306. Some settings are not available such as backup rate.

Ideas: 
1. May I suggest that you remove the sd card ? Not sure if a corrupt sd card could trigger a restart but I did have an SD card failure the first time. 
2. I did notice the device resetting when I had the programming wires connected in the wrong order. Nbritton also had some issues (programming) when the comm wires were not connected properly.
3. The behavior may be related to the language setting. You may want to try  erasing all data, resetting the device, setting language to english.

quilombodigital, 2020-05-05:
I reset to factory but the problem persisted, then I removed the sd card and it **worked**. :) ST mode and iVaps. yeah!
Even without these features you cited, is it still usable as emergency/backup ventilator?
I know this is defined by a doctor, but just for curiosity, what would be the most used mode/settings for covid patients? I just would like to let it pre-configured by default.

nbritton, 2020-05-08:
Few things to think about.

1) I noticed on my machine that if I didn't have all the JTAG wires connected (especially the ground wire) the machine would sporadically reboot on its own.

2) Rebooting like that is often a sign of insufficient power, have you checked that the power plug is securely attached?

3) Are you powering your programmer using the CPAP machine? You're not suppose to connect the power pin when using a Raspberry Pi or other SBC / software bit-banger.

4) If you enable all menu items to always be displayed then you should be able to set the extra iVAPs settings.

5) Try erasing the SD card using the machine, the option is in the clinical menus near the very bottom.

quilombodigital, 2020-05-11:
The rebooting was pretty regular, when it started ivaps, one second later. My guess is that it happened when trying to register data at the SD card. It immediately stopped rebooting when I removed the SD card. Did not tried to format it, since I think I´will not need the sd card at all... :)

ruri-baka, 2020-05-11:
Is it only rebooting after the flow generator activates?

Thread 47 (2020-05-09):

osresearch/airbreak #47: Patching SX567-0302

grf100, 2020-05-09:
I tired using ruri-baka's 0302 patch script form [here](https://github.com/ruri-baka/airbreak/blob/SX567-0302-Support/patch-airsense). I get the HACKED! message on the screen, but it did not unlock any of the extra modes. The hash on the code I have is c7d16d912816b3e5b40158b695aaff629abc9f20bb4639943748bf2ae0d8b768
I assume since this hash is difference that the offsets are different? Any guidance how how to determine the offsets on the code I have?

ruri-baka, 2020-05-11:
What model and PCB revision hardware are you testing on?

grf100, 2020-05-11:
Aircurve 10 Vauto, model 37051, PCB is Rev1.0

beast-in-black, 2021-05-13:
Sorry to necro this almost exactly a year later... I found that the 0302 patch script itself needed to be patched to get a successful flash with the new menu items (just flashed it successfully but haven't tested the new modes yet).

Attached is my modified patch based on @ruri-baka's original patch.  

[sx567-0302.patch.txt](https://github.com/osresearch/airbreak/files/6475445/sx567-0302.patch.txt)

Apply using `patch -p1 < sx567-0302.patch.txt`

TexNOz, 2021-12-15:
@beast-in-black   How did this turn out for you?

beast-in-black, 2021-12-15:
@TexNOz I've been running the patched firmware right from when I posted the
patch. Works great, including the new modes. I've kept mine on APAP mode
just to be conservative although I have increased the max pressure limit to
23 (stock tops out at 20).

ArthurMafra, 2022-03-09:
> What model and PCB revision hardware are you testing on?

Hi @ruri-baka , Let me ask you a question, how do you get to generate corresponding stubs.S for your device. I do have firmware 306 but using 401 stubs.S caused problems. Have you managed to run your airsense with sd card inserted? Vsauto, S, ST are they working? With SD card inserted I get device on infinite restart loop. SD card cannot be left on with machine running. Remove sd card allow it start but modes are not working correctly. I believe it is due to incorrect stubs.S file. What is your input? I know long time passed but I could not find 401 firmware anywhere nor generate stubs.S for 306.
Regards

ArthurMafra, 2022-03-13:
> Aircurve 10 Vauto, model 37051, PCB is Rev1.0

Hi @grf100 I know the project has been abandoned, specially with new releases getting out Airsense 11 and future aircurve.
I have been donated Airsense to treat my apnea from person here from github. Is it possible for you to share your aircurve 10 firmware since it does not contain any identifiable information? It has been noted by nbritton and also confirmed by the fact that checksums for each version always match. Thanks for much either way. Contact arthur iphone @ gmail dot com.

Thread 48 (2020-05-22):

### ISSUE TITLE
Wanted Aircurve V auto Firmware 

### ISSUE THREAD

**Issue by jimmybbk** [osresearch/airbreak#48]
Hello, I'm just wondering if someone has the Aircurve Vauto firmware. I'm looking to flash my device for sleep apnea treatment. The reason for flashing is im having a real hard time trying to get a machine from the USA to Thailand.

Thanks in advance.

https://tools.usps.com/go/TrackConfirmAction?tLabels=CH096760102US&utm_source=expected&utm_medium=email&utm_content=delivery-options&utm_campaign=trackingnotify

**Comment by osresearch** [comment]
Sorry, we don't have any rights to redistribute the vendor firmware.

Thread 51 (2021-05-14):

osresearch/airbreak #51: Possible improvement to PAP firmware itself.

Asmageddon, 2021-05-14:
For context, I am a Sleep Disordered Breathing patient, and active in a community where we discuss treatment and surrounding research.

It's a major grievance to many of us that whereas PAP machines are generally sufficient treatment in older men, younger people, women, and milder cases(where no degeneration of arousal mechanisms is present) experience only very limited benefit - of which some is inherent to the limitations of NIV, while some is regrettably down to algorithmic matters, with ResMed doing much worse than its competitor, Phillips Respironics.

Specifically, the following features would likely make a large difference:

 * Exhale Support - something similar to [Phillips Respironics FLEX features](https://cdn.discordapp.com/attachments/749382095113289800/829255676764094504/unknown.png), which essentially reduce pressure during exhale to alleviate expiratory overpressure buildup contributing to exhalatory intolerance without compromising the capacity of treatment to stent airways open. This would especially be important for a large share of patients who have narrow nasal cavities.
 * Pressure support waveform contour modification - while ResMed's EasyBreathe is very tolerable, it is not as effective as steeper pressure support curves, both in terms of preventing the need for the body to escalate respiratory effort, and in terms of elevating airway pressure during inhalation to maintain the capacity of treatment to stent the airway.
 * Disabling ASV mode backup rate - persistent, neurological central apnea is rare in SDB patients, whereas treatment-emergent central apneas diminish and disappear as the body adjusts to treatment, with the backup rate instead picking up post-arousal drops in ventilation caused by a drop in CO2, and preventing transition back to voluntary breathing control.
 * Making it possible to use a narrower min and max PS range in ASV mode, rather than mandating max PS to be at least min PS plus 5cmH2O

Of course, this is not a finite list, and much more could be improved, but past the above, I'm not sure if there's anything I'd guess likely to be possible to easily integrate into existing firmware via reverse engineering.

Drmaestro, 2021-05-14:
Hi,

You might have observed that there has been no recent activity by the developers for a long time and as such, it seems that the project is practically abandoned. I had contacted one developer 8-9 months ago and he told me that there was no real reason to go on with the project as the main aim was to prove that a CPAP unit can be used as a ventilator in an emergency situation (and they did prove that by the modification) and also the projected ventilator shortages never happened. Altering the main firmware for other purposes, like enabling other modes, would probably create legal troubles for them (copyright issues and also potential harm to patients using these mods). Of course, new developers can always continue from where they left, but from what I have observed in the last 9 months, there is very little to almost no interest in the project. (I don't want to create an air of negativity and would be very happy to see some more activity but that seems to be the truth for now).

The exhale support already exists in Res Med 10 devices, however it is limited to 3 choices (1-3 cm H20). As such, it is a limited form of BiPAP. If you want more flexibility, then the manufacturer wants you to buy their BiPAP device...

Asmageddon, 2021-05-14:
Hi @Drmaestro, thanks for the reply. The airbreak project already does unlock all modes, a feature I've taken advantage of. Unfortunately, the Expiratory Pressure Relief feature is not actual exhale support, but rather a limited form of pressure support(which is essentially inhale support). I already run my device in bilevel mode, but... it's not really enough for my case, nor for the cases of many other people. The worse nasal breathing, the more EPAP is needed, and the less EPAP can be tolerated. I had high hopes for ASV, but the backup rate just hurts the efficacy so badly. 

Ultimately, PAP is merely management, and the ultimate goal is skeletal surgery(and/or whatever adjunct surgeries are necessary), but not everyone has access to such treatment. Improving the algorithms on ResMed devices could potentially save the lives of at least a few of the people I know from inescapable fatigue.

zhuhongchao, 2021-06-27:
> Hi @Drmaestro, thanks for the reply. The airbreak project already does unlock all modes, a feature I've taken advantage of. Unfortunately, the Expiratory Pressure Relief feature is not actual exhale [...]

I have followed the instructions to unlock the ASV and other modes, but the parameters in the menu are incomplete and some of them cannot be set, did you solve this problem? (trigger, cycle, Backup rate, etc)

Asmageddon, 2021-06-30:
The ASV mode doesn't allow configuring trigger and cycle, and I believe the backup rate setting is for iVAPS, not ASV, in which backup rate is mandatory. I've personally not had success with the unlocked ASV mode.

jlm255, 2021-09-20:
Asmageddon, I am an SDB sufferer as well, RERAS, not apneas, and I was hoping to use this firmware to be able to fiddle with the EPAP beyond the EPR of 3 for the Airsense 10. Would it accomplish this?

Thanks!

chuckhacker, 2021-11-14:
Trigger and cycle are for BiPap modes:

https://www.youtube.com/watch?v=ts9lNJ2g1IE

Asmageddon, 2022-04-23:
I've recently come back around to this idea, particularly hoping to disable the ASV mode backup rate, which I hope could help me address my horrible residual sleep fragmentation on BiPAP modes.

@osresearch @wormyrocks @colinoflynn If you could help me with any of the notes not uploaded to this project's github, or pitch some ideas about how I could possibly approach debugging a running device to identify the code path or variable responsible for this, I would be deeply grateful.

macka-the, 2024-02-05:
Hi, I am sufferer of same sleep fragmentation and been wringing my machines out and closely looking at algorithms. As well as an AS10 I have an interesting machine I have not seen many investigating yet. It is a Lowenstein Prisma 20a. I believe you may be starting with an inferior base for all your efforts. The Prisma is equipped with way better hardware and design IMO. The algorithms are way better as well. The company has built its knowledge and I believe it algorithms on hospital ventilators and it shows. A base model APAP/CPAP offers 3 comfort setting which leverage bilevel and trilevel modes of higher models. The most interesting is the trilevel which they call softpap 3. This mode gives pressure support of 4 and switches up the algorithm as different stages are reached in pressure. Also the algorithm delivers ipap pressure by the time inspiration begins not mid-way or even at the end like Resmed and others. This makes a difference in smoother delivery at more appropriate times which benefits narrow nasal cavities rather than the late rush of air which just aggravates as pressures rise.
The company has a flashing tool and all models in a range have one firmware. You can see the vacant menu locations. Parts of higher modes are used for comfort provision.

jlm255, 2024-02-05:
Sounds intriguing, where/how can I get one? I just buy my machines, going
through insurance is a nightmare.

macka-the, 2024-02-06:
I am in Australia, we have to buy our machines. Problem is some of these companies come from hospital ventilator and associated equipment industry IMO. There is a lot of price gouging going on, maybe because of the Insurance model in other countries as well. Government health is huge business. Look up the ventilator contracts Phillips had with US gov. Money thrown at them and then the abuse is incredible. 
Anyway, you can get the German made Prisma in Australia and Europe, but the cheapest by far is if you can get one out of India. I would like to get my hands on the PrismaLab. It is the top model with every mode. It has real time data monitoring and ability to control via network with smoothed transitions so a sleep tech can move you between modes without disturbing you.
These are unavailable in the US. They are far superior IMO. They are being kept out by FDA I believe, must have not greased the right palms.

jlm255, 2024-02-06:
Dang that sucks. I'd like to get your contact info somehow.

I bought a Resvent from China because I wanted to try volume assured (iVaps
EVaps whatever). It basically keeps my pressures near 4 but somehow forces
a breath if my breathing drops below a set value. This seems to be just as
effective or more so, but what I think I am finding is that my deep sleep
requires different values than REM so a better algorith or sleep tech to
figure things out sounds great.

I have had UPPP surgery, MMA surgery, and 2 rounds of tongue radiofrequency
ablation and I think my apneas are cured but without a doubt I still have
some strange breathing problem. After all the surgeries, I tried going
without CPAP for a month and eventually things were going downhill again.

My sleep and life have improved a lot. Before all this my life was really
really in a dark spot. Everything was falling apart (job / family / etc)

jlm255, 2024-02-06:
I think for the first half the night I'm better off without the CPAP. But
then the REM half I need it desperately.

Asmageddon, 2024-02-17:
> The company has a flashing tool and all models in a range have one firmware. You can see the vacant menu locations. Parts of higher modes are used for comfort provision.

Wait, are you saying the prisma devices are hackable by default? 

Anyway, I've experimented with both trilevel and with fasted PS rise time in my custom firmware, the problem with fast rise time is that it becomes almost impossible to detect the actual end of breath, so you end up causing horrid asynchrony, and I wasn't able to solve this problem. Trilevel actually improves comfort, but also has some challenges.

I'm rather interested in Prisma's rapid pressure response due to a valve-based design, but if they solve the two above issues, their devices might actually be great.

macka-the, 2024-02-17:
> Wait, are you saying the prisma devices are hackable by default?

Maybe, all I know is anyone can see the link to firmware updates for every model and a link to a flashing tool of some type. There is an unused micro usb port on the machine. Communications modules are available.
I have a lower end model and it has bi-level and trilevel function masquerading as comfort features. The menus have lots of spare spaces and all models in that one range share user & service manuals.
Don't know what protections are at chip level but the service manual says to enter service mode and simply enter serial number on side of machine when performing a mainboard replacement

jlm255, 2024-02-17:
How fast is fast? I'm currently using 900ms

jlm255, 2024-02-17:
My breathing slows down too much during sleep so I have back up breathing
rate, fiddling with rise time, and the length of time CPAP machine waits to
increase pressure to try to force a breath (on resvent they label it Ti
which is confusing) I was wondering if instead of doing this, what if we
breathed more concentrated oxygen. Would this make up for the slow
breathing rate? Thoughts please.

jlm255, 2024-02-18:
> Unless you have neurological sleep apnea, do not enable backup rate. If
> your body pauses breathing, it's doing it because you are OVER-ventilated.
> Breathing is supposed to be slower and shallower during sleep.
>
> Also, lack of oxygen is not the problem. The problem with sleep disordered
> breathing is the sleep fragmentation caused by the body's reaction to
> escalating airway resistance. Oxygen doesn't matter much.

I would have said the same thing, but recently I was reading this guys blog
and it rocked my world:

https://www.cpaphealthissues.com/2019/06/ideal-body-weight-cpap-bilevel.html

I am someone who has never registered an AHI over 2 (on the CPAP) from
before my sleep apnea diagnosis, and through surgeries, and to the present
day. My sleep lab test showed an AHI of 7 and an RDI of 30. So in general
my obstructions have always been pretty minimal, but it has been
fragmenting the hell out of my sleep since birth. If you look at my fitbit
data, which I know isn't perfect, you can see how fragmented my sleep is.

My pressures are usually from 4 to 6, I actually think that a pressure of 2
might be enough for me, but very hard to find a CPAP that goes that low.
There is no question in my mind that when the CPAP is blowing air into me
like crazy that it also fragments my sleep.

While I am not positive yet, fiddling with Ti and breathing rates etc does
seem promising. I have had some phenomenal days where I didn't know it was
possible to feel so happy. But I can't get it to 7 days a week. I would say
on average I can get one "perfect" day a week, 5 very functional days, and
1 day where I am very "off" and sometimes "barely surviving" but it seems
like those days are getting less frequent as I seem to be honing in on
which numbers will really prevent a disastrous night.

macka-the, 2024-06-23:
@Asmageddon 

I now have Prisma30ST I found cheap. It has a mode aPCV I was after for same reasons as you. What I didn't know I was getting as well, was all the usual S T ST & auto ST modes, but with the addition of volume assurance on each of them.

So you can set your usual bi-level mode but with a Vt target to be maintained. The sensitivity is driven by looking at every single breath, 5 breaths, or 8 breaths. Timing on trigger, InRamp, exRamp. Choice of 3 EEPAP levels or none. Can have a variable ps and epap.
Backup is part of aPCV and I have worked around it set at 10. It has come in handy for carrying me through a flow limited period and can save the arousal.

I have the 25ST as well and it offers everything without the volume assurance. Still very good in auto S/T mode. I have found the backup quite handy in this machine set to 10 also. Synchronicity is nowhere near as easily broken in the Lowensteins as Resmed imo.
The machines seem to follow and adapt very well to erratic sponteanous breathing and then pickup again. The timing adjustments are also very good. EEPAP is essential imo to solving a lot of issues. I also use a series of flowrate hacks to get that at tolerable levels then adjust machine from there. I have intolerance for flow over a certain rate. If you breach this rate there is nothing can be done to make therapy workable. I believe have seen this in many individuals. You must approach flowrate as any other adjustment that has a perfect setting for every individual.

My next project is to get a hold of a Luisa. Ultimate in home ventilators.
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

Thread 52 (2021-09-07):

osresearch/airbreak #52: line 63 postboot error invalid command name (Help me)

msdgd, 2021-09-07:
I followed all the instructions, such an error came in the flashing part. device looped in "resmed" splash screen. Installing the backup 32.bin fixes it, but I couldn't hack it, can you help me?  @nbritton @enjrolas @redpath  @osresearch  @colinoflynn @graver  @beats-in-black 

https://gfycat.com/warpedreflectingbarasinga

`[root@fedora scripts]# telnet localhost 4444
Trying ::1...
telnet: connect to address ::1: Connection refused
Trying 127.0.0.1...
Connected to localhost.
Escape character is '^]'.
Open On-Chip Debugger
> flash_new stm32-unlocked.bin
Unable to match requested speed 2000 kHz, using 1800 kHz
Unable to match requested speed 2000 kHz, using 1800 kHz
target halted due to debug-request, current mode: Thread 
xPSR: 0x01000000 pc: 0x0800021c msp: 0x2000f000
Tickling watchdog...
device id = 0x10076413
flash size = 1024 kbytes
Resetting device...
Unable to match requested speed 2000 kHz, using 1800 kHz
Unable to match requested speed 2000 kHz, using 1800 kHz
target halted due to debug-request, current mode: Thread 
xPSR: 0x01000000 pc: 0x0800021c msp: 0x2000f000
Overwriting flash memory...
device id = 0x10076413
flash size = 1024 kbytes
Verifying that flash was written properly...
Unable to match requested speed 2000 kHz, using 1800 kHz
Unable to match requested speed 2000 kHz, using 1800 kHz
target halted due to debug-request, current mode: Thread 
xPSR: 0x01000000 pc: 0x0800021c msp: 0x2000f000
Resetting watchdog bit...
Unable to match requested speed 2000 kHz, using 1800 kHz
Unable to match requested speed 2000 kHz, using 1800 kHz
Writing magic numbers back into RCC memory...
Booting device...
tcl/airsense.cfg:63: Error: invalid command name "postboot"
in procedure 'flash_new' 
at file "tcl/airsense.cfg", line 63
`

msdgd, 2021-09-07:
If I send you my st32.bin file via e-mail, would you mind if you patch it and send it?

msdgd, 2021-09-07:
It gives the same error when restoring/flashing the stm32.bin file, but the device returns to normal. restarts are interrupted. 

`flash_new stm32.bin
Unable to match requested speed 2000 kHz, using 1800 kHz
Unable to match requested speed 2000 kHz, using 1800 kHz
target halted due to debug-request, current mode: Thread 
xPSR: 0x01000000 pc: 0x0800021c msp: 0x2000f000
Tickling watchdog...
device id = 0x10076413
flash size = 1024 kbytes
Resetting device...
Unable to match requested speed 2000 kHz, using 1800 kHz
Unable to match requested speed 2000 kHz, using 1800 kHz
target halted due to debug-request, current mode: Thread 
xPSR: 0x01000000 pc: 0x0800021c msp: 0x2000f000
Overwriting flash memory...
device id = 0x10076413
flash size = 1024 kbytes
Verifying that flash was written properly...
Unable to match requested speed 2000 kHz, using 1800 kHz
Unable to match requested speed 2000 kHz, using 1800 kHz
target halted due to debug-request, current mode: Thread 
xPSR: 0x01000000 pc: 0x0800021c msp: 0x2000f000
Resetting watchdog bit...
Unable to match requested speed 2000 kHz, using 1800 kHz
Unable to match requested speed 2000 kHz, using 1800 kHz
Writing magic numbers back into RCC memory...
Booting device...
tcl/airsense.cfg:63: Error: invalid command name "postboot"
in procedure 'flash_new' 
at file "tcl/airsense.cfg", line 63
> 

`

msdgd, 2021-09-07:
It is normal?

`─(kali㉿kali)-[/media/kali/Lexar]
└─$ sha256sum stm32.bin
533b91127aa22e05b933db203ad56c449dc12a8c3fd62f57bd88c472a8061775  stm32.bin
                                                                             
┌──(kali㉿kali)-[/media/kali/Lexar]
└─$ sha256sum stm32-unlocked.bin
3ef08b46768c9a3bb46805c61c41464023f7b18f8deee102946bf4c7ceaa1255  stm32-unlocked.bin
`

msdgd, 2021-09-07:
or Can you send me the ready stm32-unlocked.bin file to I make flash

msdgd, 2021-09-08:
or there is no problem in the patching part, is there a problem in the flashing part?  because it gives postboot error 

`[root@fedora scripts]# ./patch-airsense stm32.bin stm32-unlocked.bin
stm32.bin: Tamam
patching 000000f0
patching 00017500
patching 0001a540
patching 0001b860
Including breath.bin
patching 000bb734
Including graph.bin
patching 000fd000
patching 000f9c88
patching 00004fa8
patching 00004fc4
patching 00007eb0
patching 00007ee8
patching 00007ecc
patching 000084a8
patching 00008590
patching 00066470
patching 000050d0
patching 0000817c
patching 00008198
patching 00004f9c
patching 00004fb8
patching 00007ec0
patching 00007f14
patching 00007ef8
patching 00007f30
patching 00004fd4
patching 00007f68
patching 0000802c
patching 00008048
patching 00008064
patching 000080b8
patching 0000809c
patching 000080d4
patching 000080f0
patching 00008128
patching 00008144
patching 00008160
patching 00017588
fatal: bir git deposu (veya üst dizinlerinden birisi) değil: .git
patching 00017764
3ef08b46768c9a3bb46805c61c41464023f7b18f8deee102946bf4c7ceaa1255  stm32-unlocked.bin
`

jasonminsookim, 2021-09-24:
Hey I have had the same exact problem as you. I've used the pull request from dblunk88 with SX567-0306. I'll keep trying to debug this.

jasonminsookim, 2021-09-24:
@msdgd I think I finally solved it! Here are the steps that I took to get it working.

1) Instead of cloning this git repo, clone the pull request from @dblunk88
```
git clone https://github.com/dblunk88/airbreak
```

2) I also had to comment out the path_code function in the path-airsense script
```
# patch_code() {
# 	#if you want to add the extra breath mode
# 	BUILD_FLAGS=$(( BUILD_FLAGS | (1 << 0) ))
# 	if [ -r breath.bin ] && [ $version = "401" ] ; then
# 		echo "Including breath.bin"
# 		cat breath.bin | patch 0xbb734 || die "binary patch failed"
# 	elif [ -r breath.bin ] && [ $version = "306" ] ; then
#                 echo "Including breath.bin"
#                 cat breath.bin | patch 0xbb4d4 || die "binary patch failed"
# 	else
# 		die "breath.bin not found, did you run make?"
# 	fi 

# 	if [ -r graph.bin ]; then
# 		echo "Including graph.bin"
# 		cat graph.bin | patch 0xfd000 || die "graph patch failed"
# 		printf '\x01\xd0\x0f\x08' | patch 0xf9c88 || die "graph fixup failed"
# 	fi
# }
```

3) Follow the instructions on https://github.com/osresearch/airbreak/blob/master/docs/firmware.md

ArthurMafra, 2022-03-09:
> It is normal?
>
> `─(kali㉿kali)-[/media/kali/Lexar] └─$ sha256sum stm32.bin 533b91127aa22e05b933db203ad56c449dc12a8c3fd62f57bd88c472a8061775 stm32.bin
>
> ┌──(kali㉿kali)-[/media/kali/Lexar] └─$ sha256sum [...]

Hi @msdgd , do you have 401 firmware? Can you share over mail of google drive? I would like to have the OEM 533.. checksum.

msdgd, 2022-03-11:
I would love to share but they said it would be a problem due to the serial number and differentiation of the device

closed 2022-03-11 by msdgd

ArthurMafra, 2022-03-11:
> I would love to share but they said it would be a problem due to the serial number and differentiation of the device

There is no problem, serial number information is not stored inside firmware as nbritton noted. I will mainly use it to fix my device. I can give you a email so you can send me the download link. Is it possible for you?

ArthurMafra, 2022-03-11:
@msdgd  Note @nbritton comment.  Please share at arthuriphone@gmail.com
[image]

adrianbureu, 2024-04-07:
I’m having this same issue. Followed the instructions by @jasonminsookim but im still getting the same error. Any ideas? @msdgd

msdgd, 2024-04-07:
> I’m having this same issue. Followed the instructions by @jasonminsookim but im still getting the same error. Any ideas? @msdgd

So, it's been a long time and I don't know the exact details. But I tried it on several virtual machines with windows. Fedora, Ubuntu, Kali Linux... Which operating system are you trying on? You also made this instruction "git clone https://github.com/dblunk88/airbreak", right? 
I remember I was trying to do some things from scratch with a clean installation.

adrianbureu, 2024-04-07:
> So, it's been a long time and I don't know the exact details. But I tried it on several virtual machines with windows. Fedora, Ubuntu, Kali Linux... Which operating system are you trying on? You [...]

Yes, I git cloned directly from there. I’m using a fresh installation of debian on my raspberry pi. But I’m skipping the patching script, just trying to flash a firmware I have.

msdgd, 2024-04-07:
how? Instead of patching your autoset stm32 file and flashing stm32.unlocked, are you flashing the vauto/asv/st stm32 file of another device instead of autoset stm32?

adrianbureu, 2024-04-07:
> how? Instead of patching your autoset stm32 file and flashing stm32.unlocked, are you flashing the vauto/asv/st stm32 file of another device instead of autoset stm32?

yes exactly, I have an asv file that I am trying to flash.

msdgd, 2024-04-08:
> > how? Instead of patching your autoset stm32 file and flashing stm32.unlocked, are you flashing the vauto/asv/st stm32 file of another device instead of autoset stm32?
> 
> yes exactly, I have an asv file that I am trying to flash.

I'm also curious about the procedure you requested, but I didn't do it. I patched my own file normally. I think flashing the file of another machine definitely requires more than the steps in this regard, since the serial numbers of the device etc. are different. So I dont know

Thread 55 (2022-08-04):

osresearch/airbreak #55: Is it safe to set a breakpoint in the breath control loop while the device is running live?

chuckhacker, 2022-08-04:
Is it safe to set a breakpoint in the breath control loop while the device is running live? Worried about damaging my device, thanks.

Asmageddon, 2022-12-07:
I'd love to know this too, so pinging some contributors who might know, @osresearch, @wormyrocks, @colinoflynn.

nbritton, 2022-12-08:
Well presumably the digital electronics are just sending PWM signals to the blower motor, so I would expect it to ether stop entirely or just keep sending the same signal. It might cause the blower to go high as a fail safe condition, as more air is better than no air, but I can't think of any obvious way that you could damage the blower, it won't spin faster than it's designed to go.

colinoflynn, 2022-12-08:
I can't comment on impact on the device long-term, but I did set tons of break-points live with no *obvious* damage (smoking electronics).

Asmageddon, 2022-12-09:
Thank you both for the replies :) 

@colinoflynn, what was the behavior of the device while the execution was stopped? Did it keep blowing air at a constant speed? What happened after resuming execution?

colinoflynn, 2022-12-09:
It's been a while, IIRC yes it just got stuck at some constant speed. The PWM etc is all running as a peripheral, so when the CPU core is stopped that is just going to be left at the last value.

Asmageddon, 2022-12-30:
So I can confirm that no harm is done to the device by halting execution, the blower stops during it, and if you stop and resume it while it's idling it'll halt again in an error function but after resuming from that it's fine. 

That said, I cannot recommend trying to debug it- it seems obvious in retrospect, but debugging decompiled firmware is ridiculously tough, and I am in awe that anyone is capable of it. 

I tried to disable backup rate(machine-initiated breaths if you pause breathing) in ASV mode, and/or add the EasyBreathe exhale slope to S mode with EasyBreathe off, but I only managed to identify where the target pressure values are written, without figuring out where they're computed or how to alter any of the behavior. Ugh.

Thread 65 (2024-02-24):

osresearch/airbreak #65: Patching firmware of existing ASV

cpapenjoyer, 2024-02-24:
Hi, I have an ASV and I'm trying to jailbreak it so I can set the maxPS value to 5 while keeping the minPS at 3.
Would I be able to achieve this by following the standard firmware patching instructions?
(By patching the official firmware of my ASV device)
Will it still function the same way, but with more freedom to set maxPS?

For more context, the ASV has solved my CA events but I've noticed my heart rate goes up whenever the PS ramps up
Thanks :)

smhc, 2024-04-09:
Were you ever successful in doing this?
I attempted to patch the 305 ASV firmware with the patches from:

https://github.com/Asmageddon/airbreak-plus/blob/master/patch-airsense#L149
https://github.com/Asmageddon/airbreak-plus/blob/master/patch-airsense#L139
https://github.com/Asmageddon/airbreak-plus/blob/master/patch-airsense#L40

(with some minor address fix ups) But had no luck. Do you have 40x ASV firmware to test with?

smhc, 2024-04-10:
I managed to patch the 5cm difference limit for asv-37043-SX567-0305.bin firmware, even though it didn't seem to allow having a difference less than 5 on first install. After messing with some other firmware it eventually worked ok - I think it required the memory erase that it sometimes does when switching firmware.

base64 xdelta patch follows:

```
JVhEWjAwNCUAAAAIABgAFwAAAAAAAAAAAAAAAAAAAABhc3YtMzcwNDMtU1g1NjctMDMwNS5iaW5h
c3YtcHMtbm8tbGltaXQtMzB4LmJpbh+LCAAAAAAAAAM74HaHlYHBCEEwMDAwAkkuBk9GNgYWhi8M
wgwngGKYcgxAOQ0UOQYGAHtlTJhOAAAAH4sIAAAAAAAAA2NgaGBmYGDSaLv99Pe/Caf/bWv7Zvsp
WY+7ocGBkYlHoyCxJDlDISWxJFHz52EVr9OXlhzZL+B9carm60A/RkaJxOIyXWNzAxNj3eAIUzNz
XQNjA1O9pMw8Pwmen5d/cs2JsZgVlipxzBRoGgODMCPDB0agXYyfGLfNBTJYGdfOZxQH0SfnMz6P
ZWCwZXz7l7Ed6BxGxq8NTN2MIEZjE1P3NWkQq/eGrDaI3nlDdipY6vxN2Y3LlACW9/WKwQAAAAAA
AIolWERaMDA0JQ==
```

JohnnyDoe777, 2025-02-21:
@smhc Was it difficult to find out which hex addresses needed to be changed to another values? I wonder if this can be changed for 37113-SX567-0401 ASV fw? How did you erase memory after flash? via the cable connected from the PC and to the device board or from the device menu? Are you using this PS limit less than 5 and is it reliable? That would work for me because now it gives me too much pressure when using nasal pillows.

smhc, 2025-02-22:
@JohnnyDoe777 I believe those edits will work on other ASV firmware revisions. Or at least you could search for the pattern and do the same replacement, or just use the same firmware. Finding the bytes required reverse engineering with the aid of some of the symbols and addresses already discovered under this project.

There's no harm in flashing bad firmware if you've got a good bin to flash if it fails. The "erase" happens on the device under certain conditions, presumably when it detects a firmware version change or some other flag signifying an erase is required. Thus a particular firmware may fail initially, but if you trigger an erase using different firmware, the original one may start working after the erase.

It worked reliably when I used it, but the lower PS didn't have effective therapy vs CPAP, and it was unnecessary once I got used to it.

JohnnyDoe777, 2025-02-22:
@smhc Thanks for the reply and the information provided. I appreciate it very much :thumbsup:

PaulEvo007, 2025-02-28:
@JohnnyDoe777 Yes those edits are working well on ASV firmware versions. Off course memory addresses will differ from one version to an other. For the AirCurve ASV SX584-0305 I had a look at the firmware and changed these in the script, activated extra debugging menu's as well and all is working well. Oh and changed also the color scheme, kind of personalization of the device. I do not have the ASV SX584-0401 firmware b.t.w. but only memory addresses for the patching will differ. 
B.t.w. changing from an APAP to ASV therapy decreased my AHI from 3.5 to 0.1

JohnnyDoe777, 2025-02-28:
Nice. It's a good your AHI so dropped. 
Are you guys using the backup frequency off as well? Do you manage to sleep through the night without waking up? That's my goal that I'm trying to achieve. I also have an AHI of around 0.00 to 0.01, but I still wake up 3 to 5 times a night here and there. I am now using the unmodified 37113-SX567-0401. I don't know if just reducing the difference between PS to less than 5 would be enough, or even turning off the backup frequency. It would be worth a try to see what that does. But unfortunately I don't know how I would derive those addresses that need to be edited in the 0401 firmware.

PaulEvo007, 2025-02-28:
@JohnnyDoe777 I'm very happy with the results and without therapy the AHI was between 15 and 20. The therapist was convinced that the apneas were purely obstructive. I was quite sure that a lot were central, so a complex apnea. Your AHI is more or less perfect and so will your SpO2. Did you monitor that during the night? Within the "apnea industry" about 95 % of the people/patients are in the obstructive category and that's a 'simple' fix, keeping the airway open. Within the category of 5% centraI sleep apnea it gets a lot complexer. Perhaps you are in that small group. For me a high sudden PS is a problem and therefore getting it lower than the standard gives me more relief and less wakening up, it takes some time for the tuning and data analytics in Oscar. If you like I can make the modifications for you so you can do some testing and tuning with a lower PS.

JohnnyDoe777, 2025-02-28:
Did I understand you correctly that you would try to make a modification to the ASV SX584-0401 fw?. Would you really do it, because it's probably not an easy thing to do? I can't ask you to do such a thing.
I also think that the sudden change in PS may be the cause of the wake up. I use pretty low pressures EPAP only 5.2 and PS min 3.2 but PS max is too high for my nasal pillow mask, which has 0 leaks and therefore doesn't need such high PS (13.4 cmH2O). If I could lower the PS max to around 11 cmH2O, it might lead to less awakenings. Some reddit people say that even that backup frequency can cause awakenings. I'm more bothered by the high PS I guess.

PaulEvo007, 2025-02-28:
@JohnnyDoe777 Yes you did understand it correctly and it's fine with me. I know the struggle for finding the right medical direction/therapy and doing some testing with a lower PS by tuning the device parameters will give direction and insights. Especially if you can have a systematic approach with changing the device parameters, data understanding and data analytics.

JohnnyDoe777, 2025-03-01:
@PaulEvo007 can you contact me at impulse9[at]tutamail.com for more instruction? Thank you

MinuteVent, 2025-03-16:
@JohnnyDoe777 I sent you an email. Thanks

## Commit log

2020-04-11 gears and unlocked image
2020-04-14 docs/evaluation: motor life question
2020-04-14 index: note viral filters in disclaimer
2020-04-14 docs: switch to material theme for automatic deployment
2020-04-15 Added suggestion to remove radio and heatbed PCB connectors
2020-04-15 updated docs to coincide with stm32.bin path in tcl script, whee
2020-04-15 docs: emphasis viral filters since internet commenters are still missing it
2020-04-15 Added differential pressure sensor to components list
2020-04-16 Add wiring example for fake stlink
2020-04-16 Update docs, fix pin number order on connector, add switch PN
2020-04-16 Add pinout details from the STM32
    Connections are sorted by GPIO bank on the STM32
2020-04-18 Add accessory edge connector PCB breakout
    [edge_connector_breakout.GBL, edge_connector_breakout.GBO, edge_connector_breakout.GBP, edge_connector_breakout.GBS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]
2020-04-18 PCB docs - Minor type fixes
2020-04-18 Add description of POWR605 stuff which resets device.
2020-04-18 Added PMIC JTAG pin mappings
2020-04-20 Improve edge connector table.
2020-04-20 Added voltage regulator info to doc
2020-04-21 Update disassembly.md
    T10 screws
2020-04-25 PCB silkscreen would be upside down way pcb plugs in. Fixed & added gerbers for OSHPark as well.
    [edge_connector_breakout.GBL, edge_connector_breakout.GBO, edge_connector_breakout.GBP, edge_connector_breakout.GBS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]
2020-04-25 acc pcb: Update silkscreen again...
    [edge_connector_breakout.GBO, edge_connector_breakout.GTO, edge_connector_breakout.pcbdoc]
2020-04-27 Update hardware.md
    Added alarm and radio boards
2020-04-28 Update hardware.md
    Updated for LCD datasheet, MCU for CAM board
